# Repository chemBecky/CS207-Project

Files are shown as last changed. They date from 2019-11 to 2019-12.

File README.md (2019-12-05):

# Auto Titrator

## Description

This project uses an Arduino to automate titrations that can be monitored by pH.  A servo motor that is attached to the stopcock of a buret will rotate to add decreasing volumes of titrant depending on the derivative (change in pH over change in volume).  The pH is measured with an electrode attached to a pH-4502c.  It is intended to be used independently of a computer at the push of the "Go" button.  An emergency "Stop" button, a red LED, a green LED, and a piezo speaker are also used to communicate information. There are six stages in the sketch: before, stabilization, large volume, small volume, drop volume, and end.  The before stage moves the servo to 0 degrees and prevents the titration from starting until the Go button is pressed.  The stabilization stage gets the initial pH reading.  The volume adding stages send different delay times for the buret to be in the Open position.  The derivative is calculated after each volume addition and compared to a threshold value to move to the next stage.  When the threshold for the drop volume stage has been exceeded, the end stage is reached. The red LED turns on and the unit beeps three times. If the user agrees that the titration is complete, they press the Stop button.  If not, they can press the Go button to go back to the drop volume stage.  If a successful titration has been achieved, a tune is played on the piezo speaker.

Video description: https://youtu.be/6Ub8dkQ-ww4

## Contents

- [/sketch](/sketch/sketch.ino): Source code for Arduino
- [/circuit and breadboard](circuit%20and%20breadboard): Circuit diagrams
- [/instructions.md](Instructions.md): Instructions for use of Auto Titrator
- [/video and pictures](video%20and%20pictures): pictures of project in action
- other sketch files: [testing servo movements to calibrate volume](/sketch_servotest/sketch_servotest.ino) and [creating a tune to play after a successful titration](/sketch_toneMelodytest/sketch_toneMelodytest.ino)

## Materials

- [ ]	Arduino UNO
- [ ]	pH meter
- [ ] pH analog reader (pH-4502c)
- [ ]	two buttons
- [ ]	two 10 kΩ resistors for buttons
- [ ]	two LEDs (red and green)
- [ ]	two 560 Ω resistors for LEDs
- [ ]	piezo speaker
- [ ]	High torque servo motor, I used MG-996R with 13 kgcm torque
- [ ]	retort stand and clamp to hold the servo motor tightly
- [ ]	wires
- [ ]	copper wire (highest gauge that will fit through servo propeller) and elastic band to attach motor to buret
- [ ]	plastic container to protect Arduino electronics (cut holes for access to buttons and servo cable)
- [ ]	potentiometer (for testing if desired)
- [ ] for the titration: buret, buret stand, stir bar, stir plate, acidic/basic solutions, pH indicator

## Build Instructions
This is the circuit for the Auto Titrator using a potentiometer as a stand-in for the pH-4502c:

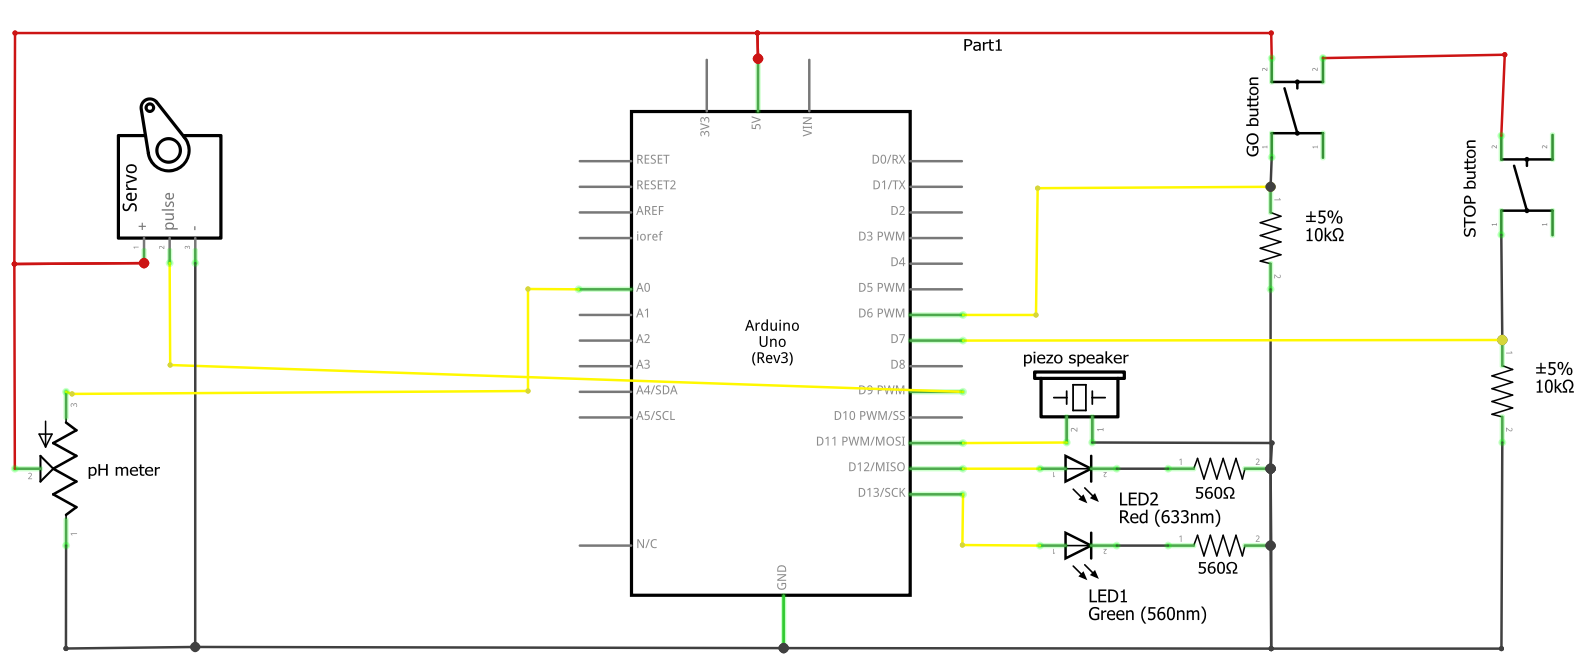
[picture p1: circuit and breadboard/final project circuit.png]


Nothing in the circuit is overly complicated.  The buttons are connected to 5V and ground through a 10 kOhm resistor.  They are in a pull-down configuration so the pin is on same side as the ground connection.  The Go button is connected to pin 6 and the Stop button is connected to pin 7.  The piezo speaker is connected to pin 11 and ground.  The LEDs are powered through pins 13 (green) and 12 (red) with 560 Ohm resistors to the ground connection.  The servo motor requires a 5V connection, a ground connection, and is connected to pin 9.  The pH-4502c needs two grounded connections, a 5V source connection, and then is connected to A0.

This is the breadboard view of the same circuit with again, a potentiometer to as a stand-in for the pH-4502c:

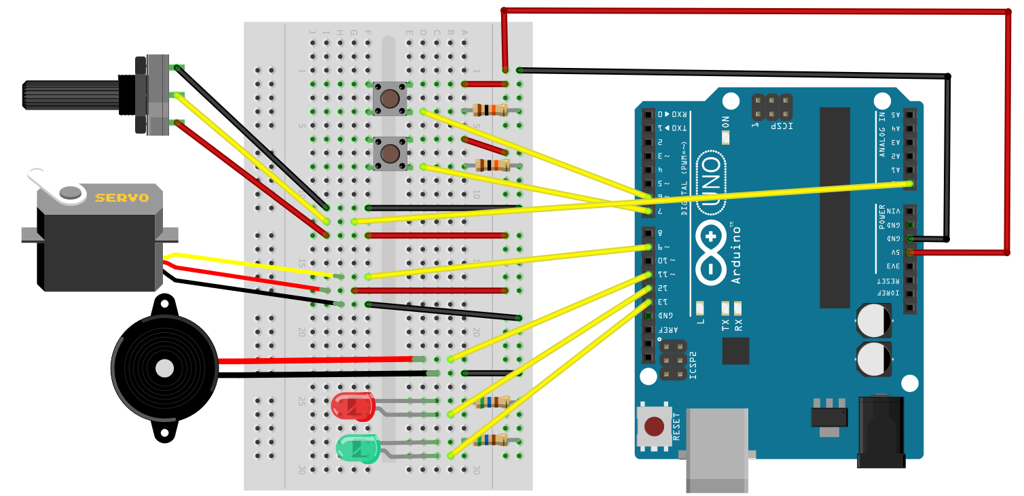
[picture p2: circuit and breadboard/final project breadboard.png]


The tough parts of the build are getting the servo/buret combination to work.  First, with the servo at 0 degrees, attach the propeller perpendicular to the motor.  Then, make sure that the screw attaching the propeller to the servo is tight.  Next, attach a stopcock to the propeller.  I found that wrapping an elastic band around the two helped with the next step.  With as large of gauge copper wire as can fit into the propeller holes, wrap the propeller and stopcock together.  I also found that lubricating the buret helped.  You will also need a retort stand and clamp to hold the motor in place during the titration.

I should also mention that the pH-4502c needs to be adjust before use.  I followed the ["How to use a pH probe and sensor](https://www.botshop.co.za/how-to-use-a-ph-probe-and-sensor/) tutorial.  Adjust the potentiometers on the board such that pH 7 reads 2.5 V and that the threshold is set as high as possible.

## Usage
Please see the [instructions](instructions.md) for a detailed account of how to use the Auto Titrator.  The [sketch](sketch/sketch.ino) only needs the default [servo.h](https://www.arduino.cc/en/reference/servo) library from Arduino.

## Credits
- [Enginerds2015](https://www.instructables.com/id/Arduino-Based-Chemical-Titration-aka-The-Titration/) for initial coding
- [AdityaMitra5102](https://github.com/AdityaMitra5102/Titrator) for servo-based buret movements
- [botshop.co.za](https://www.botshop.co.za/how-to-use-a-ph-probe-and-sensor/) for instruction to calibrate my pH-4502c
- [Fritzing (version 0.9.3)](www.fritzing.org) for the circuit and breadboard diagram creation software

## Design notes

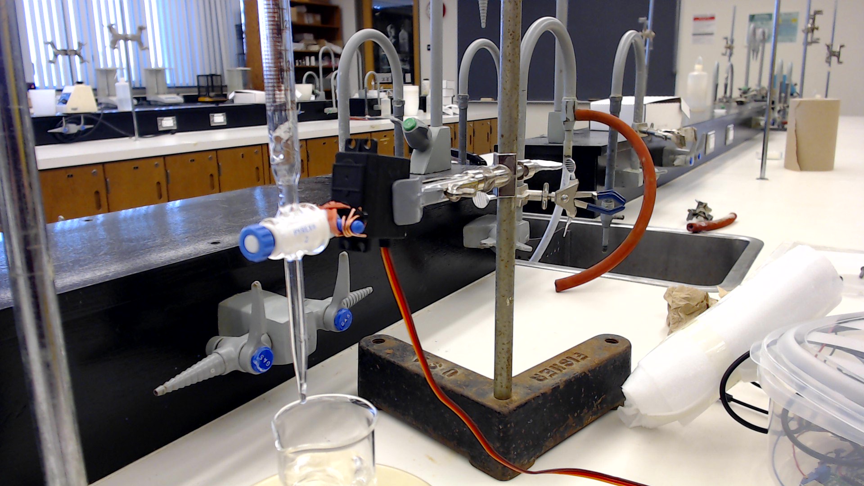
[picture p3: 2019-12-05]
video and pictures/clamp and servo.jpg

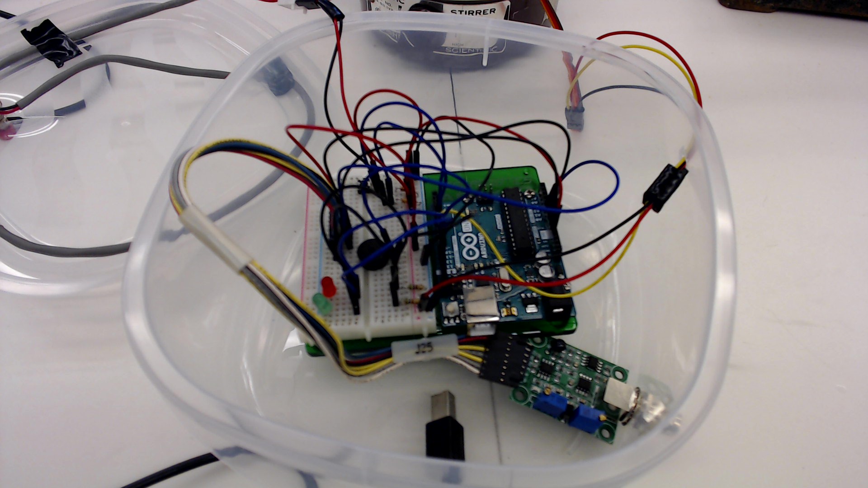
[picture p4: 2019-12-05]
video and pictures/whole circuit.jpg

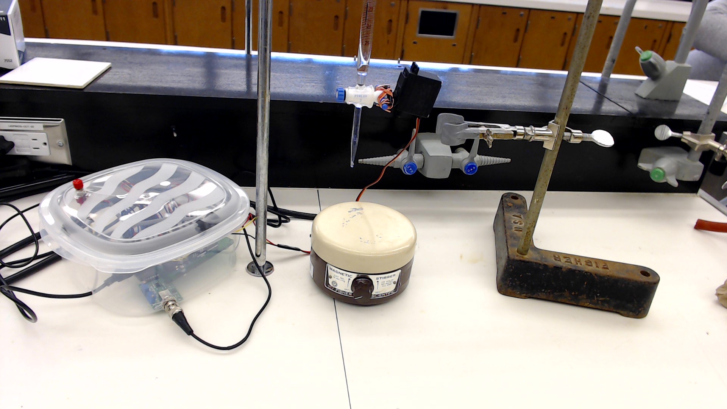
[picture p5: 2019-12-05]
video and pictures/Auto Titrator.jpg

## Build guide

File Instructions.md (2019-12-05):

#  Instructions for use of Auto Titrator

1.  Only needs to be done before the first use: Attach the servo to a stopcock.  Use the [sketch_servotest](sketch_servotest/sketch_servotest.ino) to calibrate the movements and add 1.0 mL, 0.3 mL, and a drop from the buret.  If desired, use the [sketch_toneMelodytest](sketch_toneMelodytest/sketch_toneMelodytest.ino) to create a song to play after a successful titration.  Upload [sketch.ino](/sketch/sketch.ino) code onto Arduino board with the values from the servo and tone test sketches.
2.  Attach a clean buret to a retort stand.  Insert the stopcock attached to the servo into buret and secure with o-ring and nut.  Rotate the stopcock to open and rinse buret with titrant.  Check for and remove bubbles that form.  Rotate the stopcock to the closed position.  Fill the buret with at least 20 mL of titrant.
3.  Set up the stir plate, buret height, and solution to be analyzed.  Insert the pH meter into the solution.  Start stirring the solution.
4.  Plug in the 5V adapter to power up the Arduino.  Record the initial buret reading.  The servo should move back to the starting position.
5.  Align the servo parallel to the buret. Tightly clamp the Arduino to a portable retort stand trying not to create any additional torsion or adjustment to the position of the stopcock or servo.
6.  If you are sure that everything is ready, press the GO button.  The green light will turn on to indicate that the titration is in progress.  Close the container to protect the Arduino.
7.  If there are any problems, press the STOP button.  This will stop the titration and you will need to press the GO button to restart the titration.
8.  When the Auto Titrator makes three beeps, the green light turns off, and the red light turns on, the endpoint has been reached.  If you disagree and wish for the titration to continue, press the GO button.  If you agree and wish to stop the titration, press the STOP button.
9.  At the end, the LEDs will turn off, the servo will move back to 0°, and a celebration tune will play.  Rinse the pH meter and store appropriately.   Unplug the Arduino.
10.  Unclamp the servo.  Rotate the stopcock to empty the titrant into an appropriate container.  Remove the nut and o-ring so that the stopcock can be carefully removed from the buret and cleaned.

##  Auto Titrator States:
-  **Flashing green light** - before the titration, push the GO button to start
-  **Green light** - during titration, push the STOP button for emergency stop
-  **Red light** - endpoint reached, push the GO button to continue, push the STOP button to end the titration

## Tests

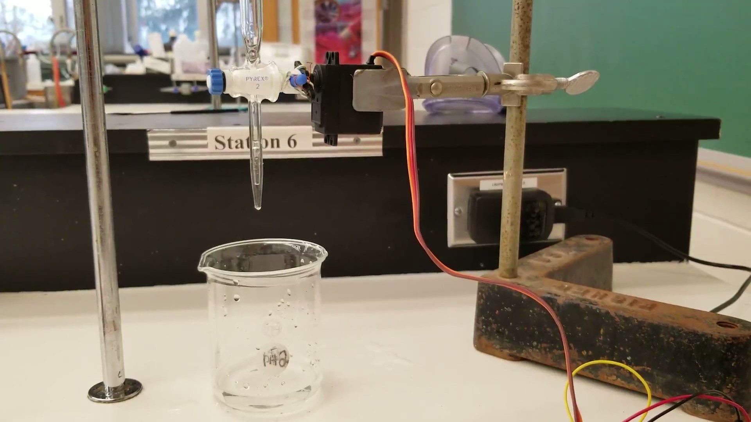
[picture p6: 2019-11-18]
video and pictures/test1 of high torque servo.jpg

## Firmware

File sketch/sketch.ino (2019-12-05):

/* CS 207 Final Project
  The Auto Titrator
  by Becky Jamieson
  December 2019
  
  This project uses an Arduino to automate titrations that can be monitored by pH.  A servo motor that 
  is attached to the stopcock of a buret will rotate to add decreasing volumes of titrant depending on
  the derivative (change in pH over change in volume).  The pH is measured with an electrode attached 
  to a pH-4502c.  It is intended to be used independently of a computer at the push of the "Go" button.
  An emergency "Stop" button, a red LED, a green LED, and a piezo speaker are also used to communicate
  information. There are six stages in the sketch: before, stabilization, large volume, small volume, 
  drop volume, and end.  The before stage moves the servo to 0 degrees and prevents the titration from 
  starting until the Go button is pressed.  The stabilization stage gets the initial pH reading.  The 
  volume adding stages send different delay times for the buret to be in the Open position.  The derivative 
  is calculated after each volume addition and compared to a threshold value to move to the next stage.
  When the threshold for the drop volume stage has been exceeded, the end stage is reached. The red LED 
  turns on and the unit beeps three times. If the user agrees that the titration is complete, they press 
  the Stop button.  If not, they can press the Go button to go back to the drop volume stage.  If a 
  successful titration has been achieved, a tune is played on the piezo speaker.

  For more instructions and circuit diagrams, please see https://github.com/chemBecky/CS207-Project
  
  
  Based on The Titration Machine by Enginerds2015
  https://www.instructables.com/id/Arduino-Based-Chemical-Titration-aka-The-Titration/
*/

#include <Servo.h>

//declare constants for pin assignments
const int pHpin = A0;
const int goButtonPin = 6;  // Go button for titration start
const int stopButtonPin = 7;  // Stop button for emergency stop
const int servoPin = 9;
const int redLED = 12;
const int greenLED = 13;
const int piezoPin = 11;

//define stages of titration
const int beforeStage = 0;
const int stabilizeStage = 1;
const int largeVolumeStage = 2;
const int smallVolumeStage = 3;
const int dropVolumeStage = 4;
const int endStage = 5;

//declare global variables
int stage = beforeStage;   // keeps the titration from starting before the button is pushed
int servoPos;   // positon of servo where 0 is a closed buret and 90 is fully open
int openDelay;   // time that the servo waits in the 'open' position
float pHold;   // stores previous pH reading
float pHnew;  
float derivative;
int goButtonState = LOW;  // pull down button, HIGH when pushed
int stopButtonState = LOW;  // pull down button

Servo servo;  // create servo object

//set up for tune to play on the piezo when titration complete
int melody[] = {
  262, 220, 233, 262, 349, 440, 392, 349, 0, 440, 392, 349, 330, 294, 392, 330, 262,
  220, 349, 392, 440, 233
};
// note durations as multiples of 1/16
int noteLength[] = { 1, 3, 1, 2, 6, 2, 2, 2, 2, 3, 1, 2, 2, 1, 3, 2, 2, 1, 11, 1, 3, 8 };


//set up the pins
void setup() {
  pinMode(pHpin, INPUT);
  pinMode(goButtonPin, INPUT);
  pinMode(stopButtonPin, INPUT);
  pinMode(redLED, OUTPUT);
  pinMode(greenLED, OUTPUT);
  pinMode(piezoPin, OUTPUT);
}

void loop() {

  stopButtonState = digitalRead(stopButtonPin);  // Use stopButton as an emergency stop

  if (stopButtonState == HIGH && stage != endStage) {   // if the emergency stop is pressed, abort titration
    analogWrite(piezoPin, 200);  // beep the piezo speaker
    delay(500);
    digitalWrite(piezoPin, 0);

    digitalWrite(greenLED, LOW); //turn off green LED
    stage = beforeStage;  
  }
    
  else if (stage == beforeStage) {
    goButtonState = digitalRead(goButtonPin);   // check if Go button has been pressed

    servo.attach(servoPin);  // for stable pH readings, only initiate servo when in use
    servoPos = servo.read();  //read current servo position
    for ( ; servoPos >= 0; servoPos --) {  // reverse servo to 0 degrees to start
      servo.write(servoPos);  
      delay(30);
    }
    servo.detach();
    
    if (goButtonState == HIGH) {
      stage = stabilizeStage;  // if GO button has been pressed, move forward with the titration
      digitalWrite(redLED, LOW);  // turn off the red LED
      digitalWrite(greenLED, HIGH);  // turn on the green LED to indicate titration start
    }

    digitalWrite(greenLED, LOW);
    delay(250);
    digitalWrite(greenLED, HIGH); //blink the LED to indicate that the Auto Titrator is standing by
    delay(250);
  }

  else if (stage == stabilizeStage) {
    delay(2000);  // let the pH stabilize
    pHold = getpH();  // get initial pH reading
    stage = largeVolumeStage;  // move forward with titration
  }

  else if (stage == largeVolumeStage) {
    openDelay = 3500;
    addTitrant(openDelay);  // rotate servo to add titrant
    pHnew = getpH();  // read pH after titrant added
    derivative = abs(pHnew - pHold) / 1.0;  // find the rate of change 
    
      if (derivative > 8) {
        stage = smallVolumeStage;  // if large change in pH, move to next stage
      }

    pHold = pHnew;  // store the new pH
  }

  else if (stage == smallVolumeStage) {
    openDelay = 600;
    addTitrant(openDelay);
    pHnew = getpH();
    derivative = abs(pHnew - pHold) / 0.3;
    
      if (derivative > 30) {
        stage = dropVolumeStage;
      }
      
    pHold = pHnew;
  }

  else if (stage == dropVolumeStage) {
    openDelay = 1;
    addTitrant(openDelay);
    delay(5000);
    pHnew = getpH();
    derivative = abs(pHnew - pHold) / 0.1;
    
      if (derivative > 500) {
        stage = endStage;  // if large change in pH, the endpoint is reached
        for(int i = 0; i < 3; i++) {
          analogWrite(piezoPin, 400);  // make three beeps on piezo speaker
          delay(500);
          digitalWrite(piezoPin, 0);
          delay(200);
        }
      }
      
    pHold = pHnew;
  }

  else if (stage == endStage) {
    digitalWrite(greenLED, LOW);  // turn off green LED
    digitalWrite(redLED, HIGH);  // turn on red LED
    goButtonState = digitalRead(goButtonPin);
    stopButtonState = digitalRead(stopButtonPin);

    if (goButtonState == HIGH) {  // if Go button pressed keep titrating 
      stage = dropVolumeStage;
      digitalWrite(redLED, LOW);  // turn off red LED
      digitalWrite(greenLED, HIGH);  // turn on green LED to indicate titration in progress
    }

    else if (stopButtonState == HIGH) {  // if the Stop button is pressed end the titration
      stage = beforeStage; 

      servo.attach(servoPin);
      for ( ; servoPos >= 0; servoPos --) {  // reverse servo to 0 degrees for next time
        servo.write(servoPos);  
        delay(25);
      }
      servo.detach();
      
      for (int note = 0; note < 22; note++) {  // play the Annie theme to celebrate completion
        int actualLength = 125 * noteLength[note];  // play each 1/16th note for 125 ms
        tone(piezoPin, melody[note], actualLength);
        
        int betweenNotes = actualLength * 1.3;  // rest for an extra 30% of time between notes
        delay(betweenNotes);
        noTone(piezoPin);  // turn off pin between notes
      }

       digitalWrite(redLED, LOW);  //turn off both LEDs
    }
  }

  delay(20);
}

//function for getting a stable, average reading from the pH meter
float getpH() {
  delay(4000);
  int total = 0;
  
  for (int i = 0; i < 10; i ++) {
    total += analogRead(pHpin); // total of 10 pH readings over one second
    delay(100); 
  }

  pHnew = total / 10;  //find the average pH value
  return pHnew;
}

//function for adding titrant
void addTitrant(int openDelay) {
  servo.attach(servoPin);
  for ( ; servoPos <= 80; servoPos ++) { 
    servo.write(servoPos);  // move servo to open
    delay(22);
  }
  
  delay(openDelay); //delay while titrant is added
  
  for ( ; servoPos >= 30; servoPos --) { 
    servo.write(servoPos);  // move servo to closed
    delay(30);
  }
  servo.detach();
}

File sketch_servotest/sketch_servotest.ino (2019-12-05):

/*
 Servo testing for Auto Titrator

 This code is for testing a servo when attached to a buret.  Adjust the reachOpenDelay and reachClosedDelay to ensure enough
 time for the servo to rotate to the correct position.  Adjust the addTitrantDelay to add the desired volume of titrant from
 the buret.  Adjust the range of angles to reduce time required to move between positions.  The servo is attached to 5V,
 ground, and output pin 9.  The servo library is required.
 
 Based on the "Sweep" example:
 by BARRAGAN <http://barraganstudio.com>
 This example code is in the public domain.

 modified 8 Nov 2013
 by Scott Fitzgerald
 http://www.arduino.cc/en/Tutorial/Sweep
*/

#include <Servo.h>

Servo servo;  // create servo object to control a servo

const int servoPin = 9;

int servoPos;    // variable to store the servo position
int reachOpenDelay = 25;  // delay to allow the servo to reach open position
int addTitrantDelay = 0; // delay while titrant added 
int reachClosedDelay = 25; // delay to allow the servo to return to closed position

void setup() {
  servo.attach(servoPin);  // attaches the servo on pin 9 to the servo object
}

void loop() {
  servoPos = servo.read();  // get the current servo position
  
  for (; servoPos <= 80; servoPos ++) { 
    servo.write(servoPos);              // tell servo to go to position in variable 'servoPos' in steps of 1 degree
    delay(reachOpenDelay);              // waits for the servo to reach the open position
  }
  
  delay(addTitrantDelay);  //delay for titrant to be added
  
  for (; servoPos >= 30; servoPos --) { 
    servo.write(servoPos);              // move servo back to closed position
    delay(reachClosedDelay);                       
  }

  delay(10000);  //10 second delay to allow buret reading
}

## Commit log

2019-10-23 Create sketch.ino
    Started writing the project sketch: assigned pins, declared variables, and set stages
2019-10-23 testing using Arduino IDE to edit
2019-10-24 added main code, missing piezo and servo, guessing slope
2019-10-29 updated if statements to get desired flow
    forgot to add digitalRead for buttons, button2 acts as an emergency stop, piezo beeps at end of titration
2019-10-30 Servo instructions added
2019-11-03 adjustments to servo movements, return to 0 deg at end
2019-11-03 servo testing sketch
2019-11-10 added servo movements and piezo beeps
2019-11-10 else statements, piezo, servo
    removed unnecessary else statements, made piezo analogWrites, fixed servo for loop delays
2019-11-10 fritzing circuit diagram
    [final project circuit.fzz]
2019-11-18 changed variable names, added tone(), emergency stop goes to beginning
    changed button variables to stopButton and goButton for clarity; added Annie theme tune at the end of a successful titration; changed emergency stop stage to go back to stage = 0
2019-11-18 piezo circuit corrected, better labels
    [final project circuit.fzz]
2019-11-21 servo delays updated
    made appropriate changes to servo movement based on testing
2019-11-21 start servo at 0, green light off, fix redundancies
    move servo to zero before starting titration, turn green LED off when emergency stop used, removed redundant boolean in else if statements
2019-11-24 servo updates
2019-11-26 pH reading stabilized
    moved pH meter to A0, only initiate servo when in use attach/detach, servo delay 22 ms, removed repetitive comments
2019-11-28 updates to servo movements
    changes to servo parameters based on real world testing
2019-11-30 stop button beep, green LED blink
    made the piezo beep when an emergency stop registers, green LED blinks to indicate that the servo is at 0 degrees and Auto Titrator is standing by
2019-11-30 flashing green LED added
2019-12-03 drop threshold, servo range, large delay, green on
    drop threshold 500, servo 30 to 80, large delay 3500, green LED on when titrating
2019-12-04 diagrams of circuit and breadboard
2019-12-04 description, table of contents, materials
2019-12-04 pics of circuit
2019-12-05 more variables to increase versatility
    split reachPosDelay into reachOpenDelay and reachClosedDelay, updated description, made servoPin variable
2019-12-05 read the current servo position
